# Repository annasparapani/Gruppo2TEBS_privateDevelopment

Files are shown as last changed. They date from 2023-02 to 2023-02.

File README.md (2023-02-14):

# GlucoSense&reg;  Project
## LTEBS Group 2 (2022-2023)

> NB this is the **private development** folder to use after the submission of Feb. 13th for further development that's not going to be graded. What we submitted and all the commits history before Feb. 13th is in [**this repo**](https://github.com/ltebs-polimi/AY2223_I_Project-2)

Hi! Welcome to our project repository. 
We are **Pedro Gianjoppe, Gabriele Paroli, Anna Sparapani** and **Pietro Zerboni** and we worked with or tutor Andrea Rescalli for the "Laboratorio di tecnologie elettroniche e biosensori", a course from professor Cerveri @PoliMi. 

We worked with a PSoC 5 microcontroller to develop a device that could perform Cylic Voltammetry (CV) and Chrono Amperommetry (CA) [^1] procedures with the aim to determine glucose concentration in a solution. 

In this repository you will find all the code we developed. Here's a guide on how to use the GlucoSense and after that you can find more detailed info about all the development steps and choices we made in the past months. We hope this paints a clear picture of our project, but please let us know if you have any doubts! 

###### Table of Contents 
1. [User Guide](#user-guide)
2. [Development Info](#development-info)
3. [References and Acknowledgements](#references-and-acknowledgements)

--------
## User Guide
The device presents a switch, a connector for the glucose strip and a LED. To use it you will also need a computer running the GUI. 
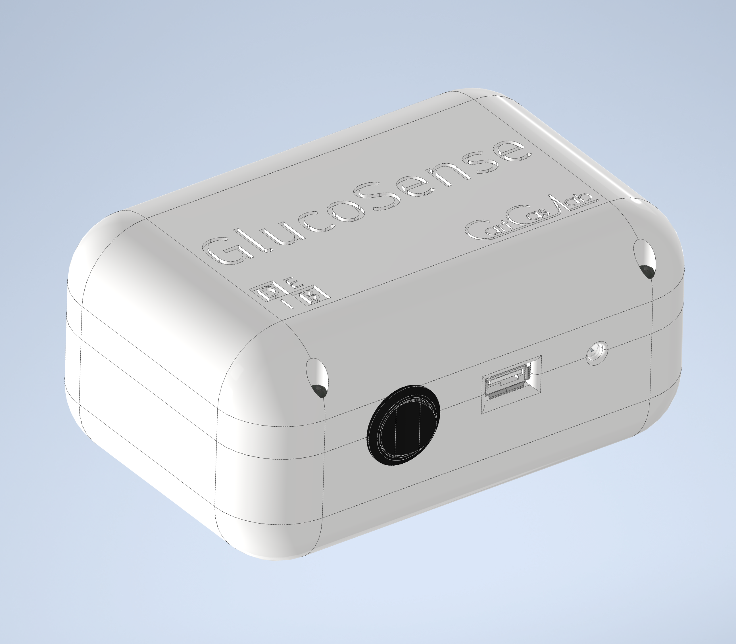
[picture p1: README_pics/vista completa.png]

1. Switch on the device, the LED should switch on
2. Start the GUI ([GUI.py](/GUI/GUI.py) file)
3. Press the `Connect to Bluetooth` button on the GUI and wait for the button to become `Disconnect from COM port`. This means that the GUI is connected to the PSoC
4. Press `TIA initialize` and wait a few seconds - *this is needed for the GUI to receive initialization data the device creates when switched on*
6. Insert a glucose strip in the connector (electrodes facing up, see [picture](#glucose-strips-and-connector))
5. Now you can start with the measurements 
   - **Option 1 : Measure Glucose**
   This allows you to perform a simple glucose measure, from the Home Screen button `Measure Glucose`. When this is pressed the device will perform a CA with standard parameters and then evaluate the glucose concentration based on the calibration curve we built.
      1. Add a drop of solution to the strip active site and make sure it turns from yellow to black
      2. Press the `Measure Glucose` button, the LED will start blinking
      3. A couple of seconds later the LED wil stop blinking and you can read the evaluated glucose concentration next to the button 
   - **Option 2 : Cyclic Voltammetry**
   This allows you to perform a CV procedure
      1. Press the `Cyclic Voltammetry` tag in the upper bar of the GUI, this will take you to the CV page
      2. Choose the parameters you want to use 
         - `Min` and `max Voltage` $\in [\pm 2500mV]$ range
         - `Scan Rate` $\in [0, 10] mV/s$ controls the speed of the procedure
         - Select the `Type of CV`, the default is a linear CV but also a Square Wave Voltammetry can be performed
         - If a SWV is chosen, select also the pulse increment and pulse height parameters
      3. Add a drop of solution to the strip active site and make sure it turns from yellow to black and wait for about 20s 
      4. Press `Start`, and wait for the procedure to finish
      5. At the end the GUI will display 
         - the graph of the measured current (mA) against the imposed voltage (mV)
         - the graph of imposed voltages (mV) against time (ms)
         - the optimal working point voltage in the bottom left corner. This is the voltage at which the biggest peak in the duck-plot is observed
   - **Option 3 : Chronoamperommetry**
      1. Press the `Chronoamperommetry` tag in the upper bar of the GUI, this will take you to the CA page
      2. Choose the parameters you want to use 
         - `Fixed Voltage` (mV) is the voltage of the low part of the square wave imposed during the CV
         - `Pulse Voltage` (mV) is the voltage of the pulse part of the CA square wave 
         - `Duration` (ms) is the period of the square wave
         - alternatively, the CA can be performed with standard parameters, which were obtained during calibration and are saved in the PSoC's EEPROM
      3. Add a drop of solution to the strip active site and make sure it turns from yellow to black and wait for about 20s 
      4. Press `Start`, and wait for the procedure to finish
      5. At the end the GUI will display 
         - the graph of the measured current (mA) against the time (ms)
         - the graph of imposed voltages (mV) against time (ms)
         - the glucose concentration based on the current at 500ms. This is accurate only if the `Pulse Voltage` is the standard one (56mV), since the calibration curve has been built with this.

If there are issues you can always disconnect and reconnect the device, as well as switching it off and then back on. Remeber that if you switch the device off, you will have to connect it again and initialize it again (pressing the `Connect to Blutooth` and `Initialize TIA` buttons). 

----
## Development Info 
1. [PsoC C Code](#1-psoc-c-code)  
   - [Files](#c-files)
   - [Interrupts](#interrupt-routines) 
2. [GUI](#2-gui)
   - [User Interface](#user-interface)
   - [Device Calibration](#device-calibration)
3. [PCB](#3-pcb)
4. [Case and Strip Interface](#4-case-and-strip-interface)
   - [Case](#case)
   - [Strip and Connector](#glucose-strips-and-connector)

Overwiew of our development stages and interactions:
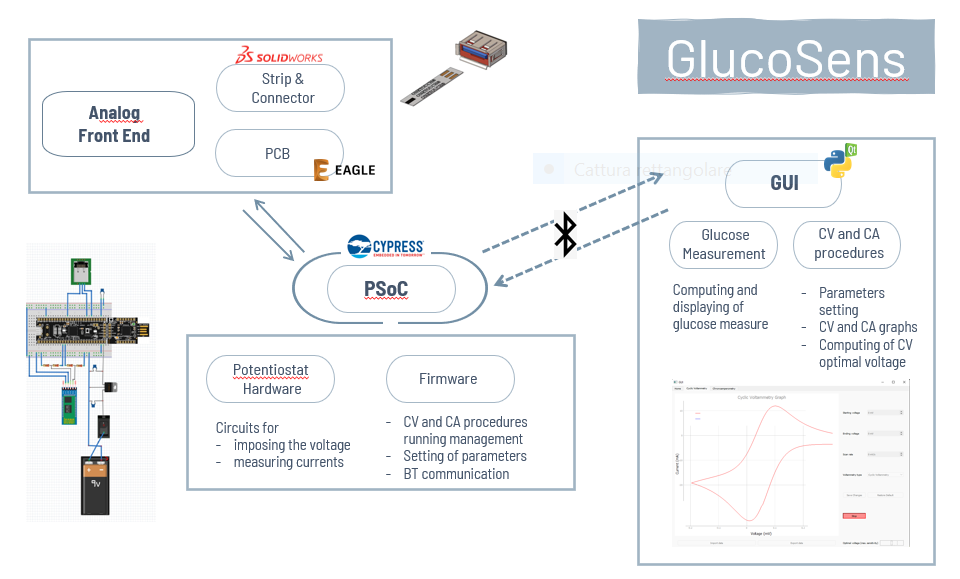
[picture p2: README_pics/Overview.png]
Overview


### 1. [PSoC C code](/PSoC_Project)
The PSoC microcontroller was programmed through its proprietary software, *PSoC creator*. The code manages all CV and CA measurements and communication with the GUI via UART Bluetooth. 
The main has a "switch cases" structure based on the input coming via BT from the GUI. Here's an example of workflow: 
1. PSoC is switched on and performs initialization procedures
2. when a byte is received on the RX of the UART BT an ISR is called, which saves it in the global variable data_buffer[]
3. when a TAIL is received on the RX of the UART BT, meaning the incoming data is finished, a flag is raised from the ISR
4. in the while(1) of the main, when the flag is raised one of the cases is entered based on data_buffer[0] and the flag is lowered
   > we are using the headers of the incoming data to switch cases in the main.c
5. the code inside the case is exectued

The code relies on a variety of .c files, which group the functions called by the main, according to their objective.

#### .c Files 

- [**`hardware_management.c`**](/PSoC_Project/PSoC_Project.cydsn/hardware_management.c) contains all functions that manage the hardware initialization, sleep, wakeup etc. during the execution of the code. The measurements and procedured rely heavily on the embedded DAC and ADC, as well as a TIA, OpAmps and other components that complete the circuit.
- [**`DAC_management.c`**](/PSoC_Project/PSoC_Project.cydsn/DAC_management.c) two DACs are be used to impose voltage (VDAC with 8 bit resolution = 16 mV resolution, and a DVDAC with 12 bits resolution ~ 1 mV resolution)
This file is called by `hardware_management.c` and simply checks which DAC is selected and performs the start, wakeup etc. function on that component (so that `hardware_management.c` does not have to check every time which DAC is selected). In our project, at this point, the user cannot select which DAC to use via GUI. Wr are always using the 8-bit VDAC; however we built the code so that for future developments, a simple change in the GUI code would allow this option.
- [**`BT_protocols.c`**](/PSoC_Project/PSoC_Project.cydsn/BT_protocols.c) this file contains the function needed to write on the BT to send data to the GUI. The reading is implemented in the BT RX ISR. 
Since when the CV and CA are performed long arrays of data have to be sent, functions in this file manage these long arrays by splitting them up in shorter arrays and sending them in consecutive iterations.
- [**`lut_protocols.c`**](/PSoC_Project/PSoC_Project.cydsn/parametric_lut.c)
the values imposed by the DAC during the procedures are either triangular waves (during CV) or a square wave (during CA). To allow a fast switching between two subsequent steps of imposing the voltage, the values are previosly saved in a Look Up Table (LUT, a global array `uint16 waveform_lut[]`). The values expressed not in mV but in levels of the DAC (255 in case of the VDAC-8 bit and 4096 in case of the DVDAC-12 bit), so they can be directly fed in input to the `DAC_SetValue(value)` API functions. 
- [**`user_inputs.c`**](/PSoC_Project/PSoC_Project.cydsn/user_inputs.c) this file contains functions that are often called by the `main.c` cases and act as a midman between the main and the technical functions contained in the previously discussed files.

#### Interrupt Routines 
- **`dacInterrupt`** called on the rising edge of the PWM wave during the CV and CA procedures, it imposes a DAC value on the counter electrode. It uses the `DAC_SetValue(uint8 value)` API function, and the input is given as a level of the DAC. The conversion from mV to DAC levels is perfomed in the GUI before sending the parameters, so that the LUT is already built in terms of DAC levels.
When the measure is finished (all the wave saved in the LUT has been imposed) it sends the data to the GUI via BT.
- **`adcInterrupt`** called on the falling edge of the PWM wave during CV and CA procedures, it reads the voltage at the working electrode and saves in in th global array `data_long[]` which will be send to the GUI at the end of the procedure.
   > **PWM called ISRs** \\
   the `dacInterrupt` and the `adcInterrupt` are called on the falling and rising edges od the PWM squared wave respectively. Since the user can selected the *Scan Rate* parammeter in the CV procedure, the speed at which the traingular wave is imposed needs to the changed. To allow this, we adapt the PWM period to the scan rate (done by a function from `user_inputs.c`)
- **`Custom_UART_BT_RX_Interrupt`** manages the RX of the BT UART. It is called every time there is an incoming byte on the RX and saves the data in the global array `data_buffer[]`. When byte equals to `TAIL` is received, it raises a flag to signal the main that there is some ready data.

### 2. GUI
#### User Interface
The Graphical User Interface (GUI) has been implemented in Python - `PyQt5`. To run it you just need to open the [GUI.py](/GUI/GUI.py) file in the GUI folder and run the .py code using the PyQt virtual environment. It is necessary to install the [`scipy`](https://pypi.org/project/scipy/), [`PyQt5`](https://pypi.org/project/PyQt5/), [`pyqtgraph`](https://pypi.org/project/pyqtgraph/), [`pyserial`](https://pypi.org/project/pyserial/) and `serial` libraries to run the code.

The GUI performs all interactions between the user (which is the patient or the doctor) and the device, since there are no buttons or LCD screens in the hardware except from the turn ON / OFF button, which can be used to restart the PSoC.

Those interactions are implemented by serial communication between the Bluetooth Module connected to PSoC and the Python `serial` library. Multithreading in PyQt was implemented to establish the connection of the COM port and also for the reading and writing data from PyQt to Bluetooth.

The GUI is divided in 3 different tabs: "Home screen", "Cyclic voltametry" and "Chronoamperometry", each one with its own funcionalities and widgets.

##### 1. Home screen
performs bluetooth connection and one-click glucose measurement (only page that the patient can access).



When the GUI is started, the connection is switched on by pressing the `Connect to Bluetooth` button which triggers the GUI to scan all serial ports by sending a specific character. When the serial port corresponding to the PSoC BT module responds with the proper character, the port is opened and the device results connected to the GUI. After that, the `TIA initialize` button is used to signal the PSoC that it can send back the values from the initialization of the TIA, in order for the GUI to calculate and store the TIA resistance value.

Below, in this same screen, the `Measure Glucose` button to performs the one-click glucose concentration measurement by performing Chronoamperometry with the default parameters stored found during calibration. Then, the proper current value is retrieved from the measurement and applied to the linear regression model obtained from the calibration of the device. The resulting value, corresponding to the glucose concentration, is displayed.

##### 2. Cyclic Voltammetry
performs and displays Cyclic or Square-Wave Voltammetry procedures with desired parameters, imports and exports measurements to external .csv files and computes optimal voltage for Chronoamperometry 
> Our idea is that this page is accessed only by a clinician who knows how to set the parameters. The patient only uses the Home page and performs simple glucose measurements.



In the CV screen, the user can choose the CV parameters (*scan rate, start and end values, type of CV*) and start the procedure. It is also possible to save the parameters in the EEPROM (`Save changes`) and retrieve parameters from the EEPROM (`Restore default`).

When the procedure button (`Start`) is pressed, the parameters are sent to the PSoC, which creates the LUT and adapts the period of the PWM. It then starts the procedure and it is possible to interrupt the measurements by pressing the same button (which now displays the label `Stop` in red). When the procedure is finished (in case it is not interrupted by the user), PSoC sends all measured values back to the GUI. The GUI receives two arrays, the first with all measured voltages and the second with the LUT (all imposed voltages), converts the values in mA and mV ranges and then plots them in two graphs: 
- The duck-plot of the Current (mA) in respect to the imposed Voltage (mV)
   > we tested the device, and obtained duck-plots for concentrations in the [50, 200] mg/L range. If you use a much higher or lower concentration the parameters the GUI allows you to choose will probably not lead to a duck-plot.
- The imposed Voltage (mV) with respect to the procedure time (ms) 

It also retrieves the optimal voltage for the Chronoamperometry by computing the value of imposed voltage for which we have the highest current measurement in absolute value (the highest or lowest peak in the duck-plot).

#### 3. Chrono Amperometry
performs and displays ChronoAmperometry procedure with desired parameters, imports and exports measurements to external file and computes the Glucose Concentration (page accessed only by the doctor).
> As for the CV page, our idea is that this page is accessed only by a clinician who knows how to set the parameters.



Very similar to the CV screen, the CA screen allows selection of CA parameters and starting of procedure and then plots the measurements data coming from the PSoC in two graphs: 
- The exponential decay plot of the Current (mA) in respect to the procedure Time (ms)
   > as for the CV, we tested the device for concentrations in the [50, 200] mg/L range.
- The imposed Voltage (mV) in respect to the to the procedure Time (ms)

It also calculates the glucose concentration by retrieving the proper current value from the measurements and appling it to the linear regression model obtained from the [calibration](#device-calibration) of the device. The resulting value, corresponding to the glucose concentration, is displayed.

Both CV and CA screens allow for **export** and **import** of data. 
- Data is exported into a `.csv` file and named with the time and date of the measure. 
- Data can be imported to be graphed in the corresponding window

Both CV and CA screens allow to **Save changes to EEPROM** and also to retrieve the **default values from EEPROM**.

#### DEVICE CALIBRATION
In order to allow the computation of the glucose concentration by means of the CA measurements, a calibration step was necessary for the device. The calibration was done using the GUI and followed the steps:
1. Perform Cyclic Voltammetry procedure to find the optimal voltage as the imposed voltage for which the measured current has maximum magnitude 

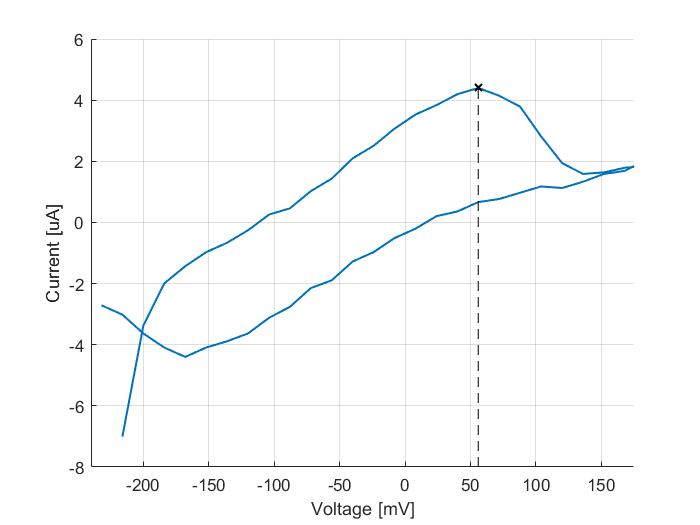
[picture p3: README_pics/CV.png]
CV to find the optimal voltage
   
   The optimal voltage was found at **56mV**

2. Set up the parameter `Pulse Voltage (ms)` of the CA as the optimal voltage from the CV

3. Perform CA procedure for 4 different solutions with known glucose concentration (50, 100, 150 and 200 mg / dL) 

4. For each resulting graph of Current (mA) over Time (ms), retrieve the current measurement at a st time stamp (current measured at 500 ms, so the 50th value, since the CA is performed with 10ms intervals) to be used in the linear regression.
Here are the current vs time graphs we obtained: 
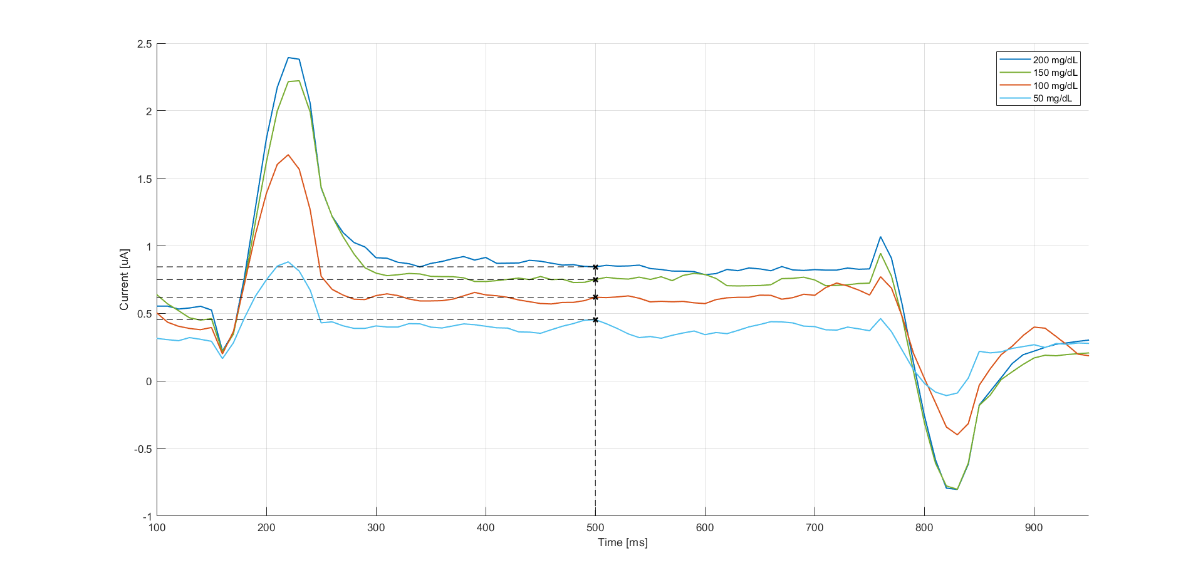
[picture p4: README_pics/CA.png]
CA for 4 glucose concentrations


6. Plot the 4 values of current measured at 500ms with respect to the known glucose concentration

7. Apply Linear Regression to find the **Calibration curve** of the device 
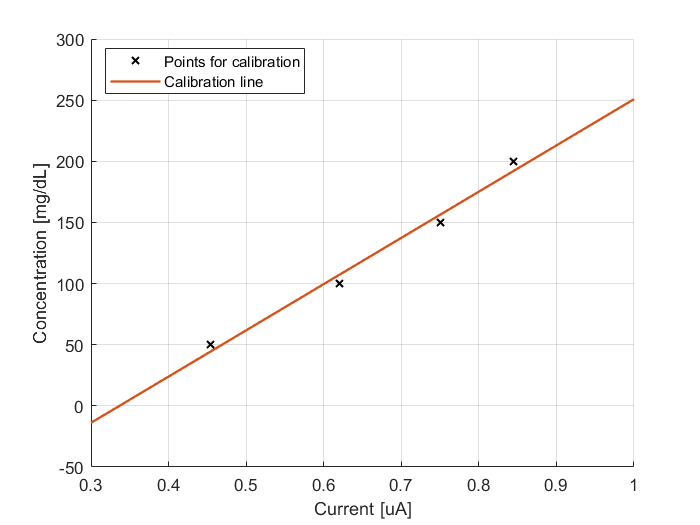
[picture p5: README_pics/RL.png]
Calibration curve


These plots and the linear regression were done in *MatLab*.

### 3. [PCB](/PCB)
Most of the electrical design needed to perform the procedures is embedded in the PSoC (DACs, ADC, TIA etc.), so the PCB only presents interface elements. 
The PCB was developed in *Eagle* by Autodesk. Here is a simplified schematic created on *Fritzing*:

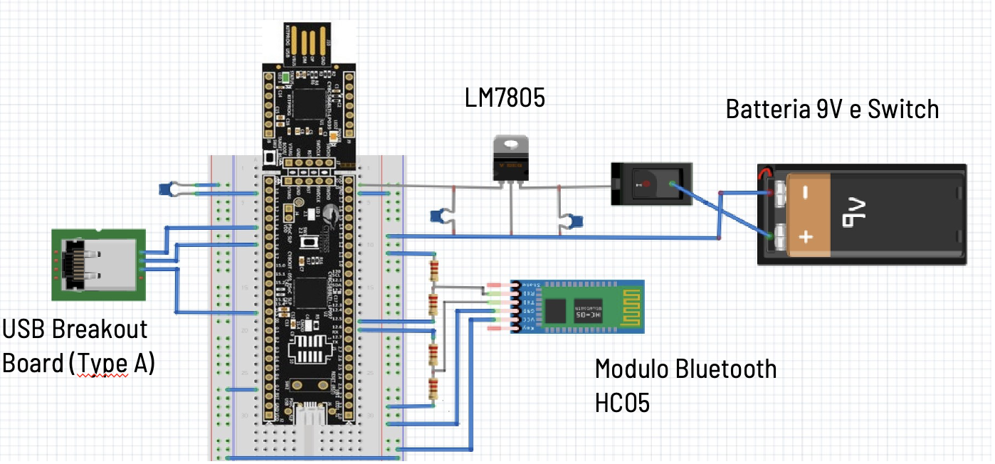
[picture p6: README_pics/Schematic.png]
Fritzing Schematic


As you can see from the image, the board includes:
1. Connections for the BT module. We use a voltage divider to lower the voltage as the TX and RX pins works at 3,3V.
2. The USB breakout board, used to interface the glucose strip with the board
3. One LED
3. The power circuit, we use a 9V DC battery and a standard linearization circuit and a switch (so that the device doesn't need to be connected to the computer running the GUI or to any other power source)

We self made the board in the lab, printing the Eagle schematic and then imprinting it on a copper covered board. We then cut it and pierced it to solder the components. We soldered directly only resistances and capacitors, and placed plugs for all other elements, so that they can be easily removed and reused by the lab.

Here's an image of our printed board 
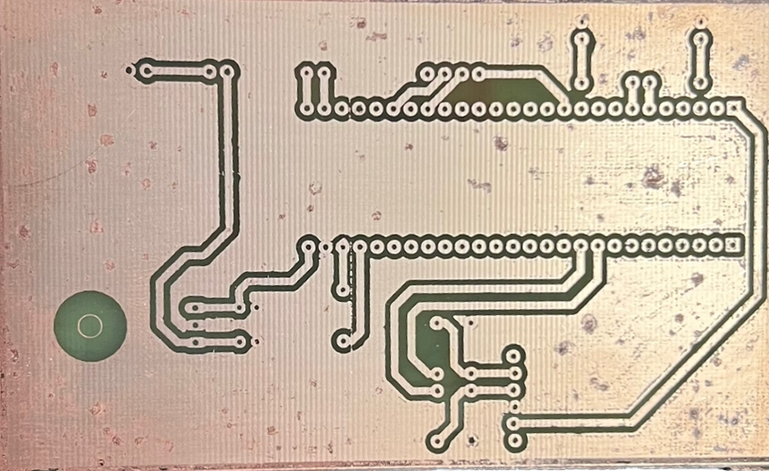
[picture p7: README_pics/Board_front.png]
Board
 

and here the back with the elements soldered on
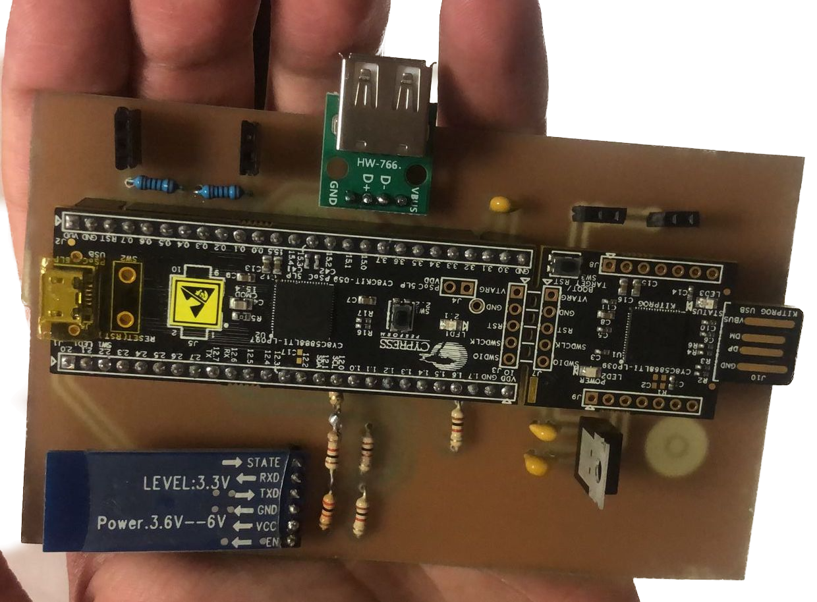
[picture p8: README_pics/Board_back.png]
Board
 

### 4. [Case and strip interface](/3D/)
Our idea for the case was to have a clean design with only the essential interface elements on the outside. As you can see from the following pics the device presents itself as a box with a switch, connector for the glucose strip, and a LED on the side. 
All 3D modeling was performed using *Autodesk Inventor*, followed by slicing of all parts using *Cura* software. Finally, the parts were 3D printed in PLA using an *Ultimaker 3*.

#### Case
The case was designed and constructed to be compact while allowing separate and easy access to both the PSoC and battery. The PSoC can be accessed by removing the four screws holding the top portion of the case in place, providing access to the PCB and components soldered onto it. 
A dedicated compartment was created in the lower portion of the case to hold the battery, and access to it can be obtained by removing a cover held in place by two screws.
Case Open
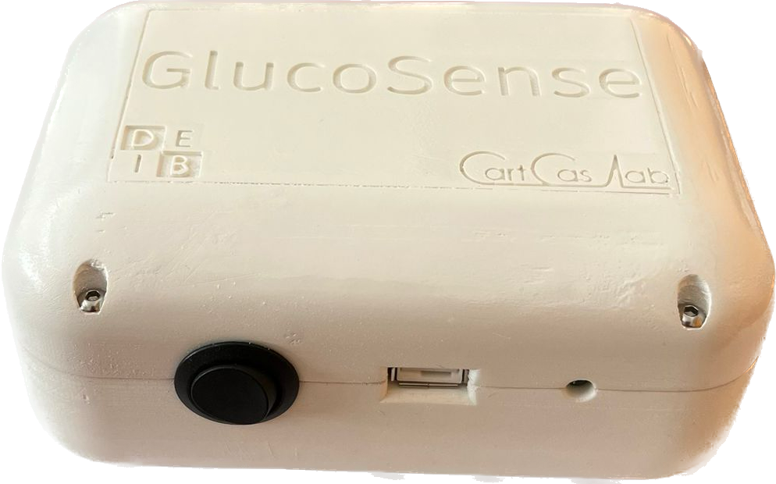
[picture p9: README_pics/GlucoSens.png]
GlucoSens


#### Glucose strips and connector 
We chose the [*OneTouch Ultra*](https://www.amazon.it/One-Touch-Ultra-Strisce-Test/dp/B002FU5WHY/ref=sr_1_1?keywords=one+touch+ultra+strisce&qid=1676288893&sr=8-1) glucose strips to develop our device around. They are readily available on Amazon, quite cheap and provide three electrodes easily accessible. 

To have an easy and realiable way to interface the strips with the device electrical pins, we decided to adapt a female USB connector so that three out of four of the electrical lines of the USB would turn into our electrodes lines.
We designed and 3D printed a custom adapter, which leaves the correct space to insert the strip and ensures electrical contact of the electrodes on the strip with three electrodes of the USB, as you can see from the following diagram.
Connector

---
### References and Acknowledgements

Our work was inspired by the previous work of Lopin et al. (2018) [^2], which proposed to use the PSoC as a potentiostat and developed PSoC anf GUI code to perform CV and CA procedures.
Our requirements differ in some ways from the aim of Lopin et al., so we had to adapt and change significantly our development, but their code was of great help.

For the choice of the OneTouch Ultra as for glucose strips, we relied on the project by M. Bindhammer, published on *hackaday.io* [^3]. The project is then developed on an ArduinoUNO microcontroller. 

We would like to thank our tutor Andrea Rescalli for his help and insights, as well as the lab's team. 

[^1]:"A Practical Beginner’s Guide to Cyclic Voltammetry"
Noémie Elgrishi, Kelley J. Rountree, Brian D. McCarthy, Eric S. Rountree, Thomas T. Eisenhart, and Jillian L. Dempsey
Journal of Chemical Education 2018 95 (2), 197-206
DOI: 10.1021/acs.jchemed.7b00361

[^2]:"PSoC-Stat: A single chip open source potentiostat based on a Programmable System on a Chip"
Lopin P, Lopin KV (2018) PSoC-Stat: A single chip open source potentiostat based on a Programmable System on a Chip. PLOS ONE 13(7): e0201353. https://doi.org/10.1371/journal.pone.0201353 

[^3]:https://hackaday.io/project/11719-open-source-arduino-blood-glucose-meter-shield
# Gruppo2TEBS_privateDevelopment

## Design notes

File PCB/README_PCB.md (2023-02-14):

## READ ME - PCB

PCB mono layer.

### SCHEMATICO:
-Spostare SWTICH1 sulla SX in modo che sia accanto alla brakout board -> altrimenti dobbiamo tirare dei jumper oltre la scheda

### BOARD:
- IMpostato uno spacing di almeno 1mm tra route e ground plane
- SWITCH1 da sposatre
- BLE_MODULE, il pin 1 e 6 non ci servono

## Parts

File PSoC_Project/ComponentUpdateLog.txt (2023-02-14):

Last Modified Date & Time: 01/15/2023 09:01:02

PSoC_Project: PSoC_Project.cydwr
	LIN_Dynamic [v5.0] to [v6.0]

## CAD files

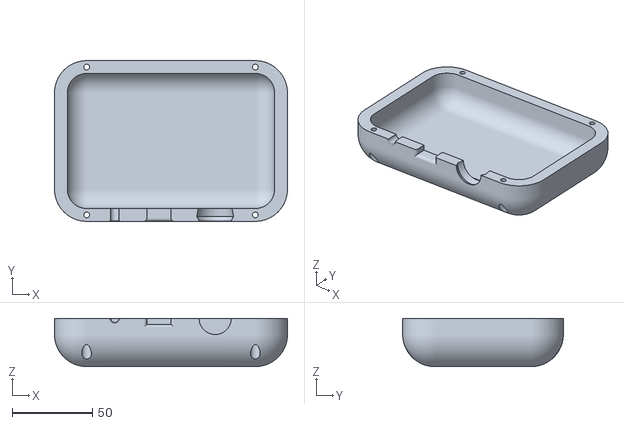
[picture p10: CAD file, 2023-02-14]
3D/Case - Cura/Case superiore.stl
145.0 x 100.0 x 30.0

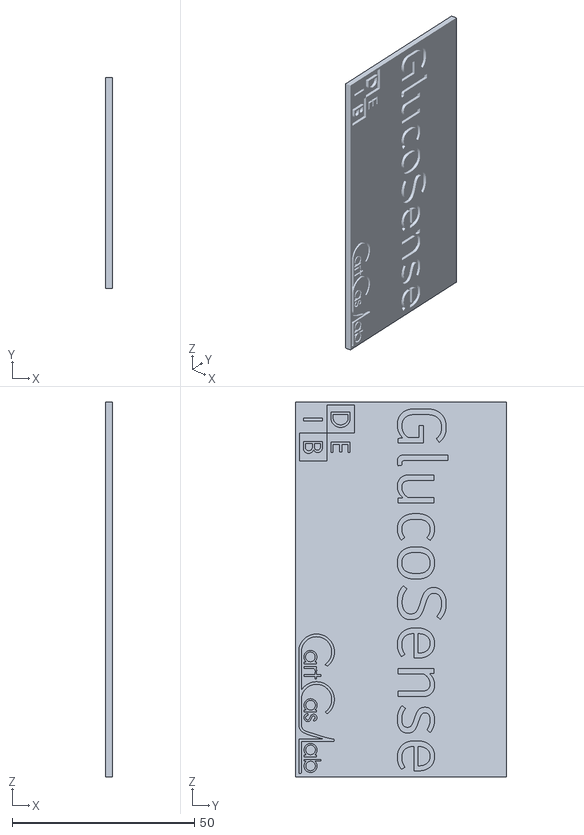
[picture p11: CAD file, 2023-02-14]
3D/Case - Cura/Targhetta.stl
2.00 x 58.0 x 103.0

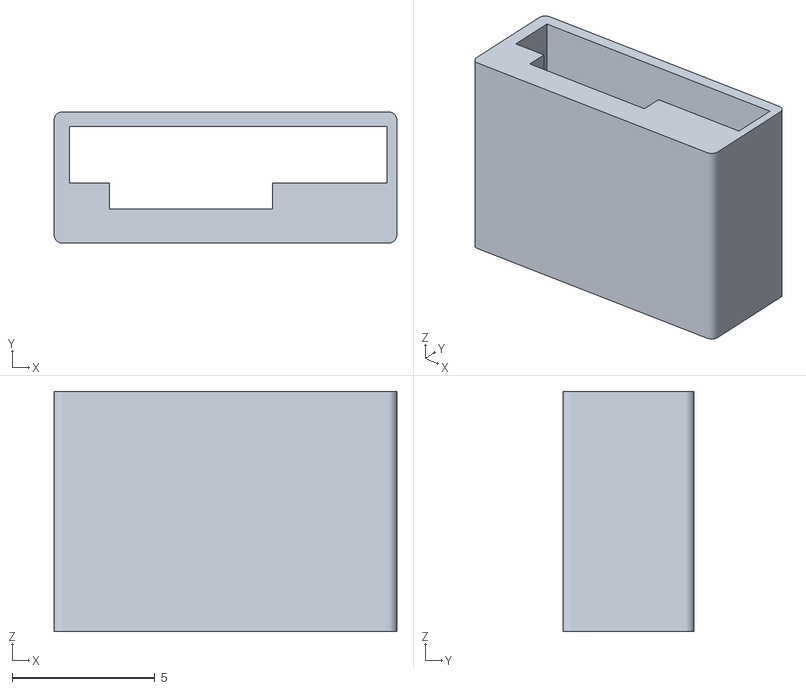
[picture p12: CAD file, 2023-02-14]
3D/Case - Cura/Adattatore.stl
12.0 x 4.60 x 8.40

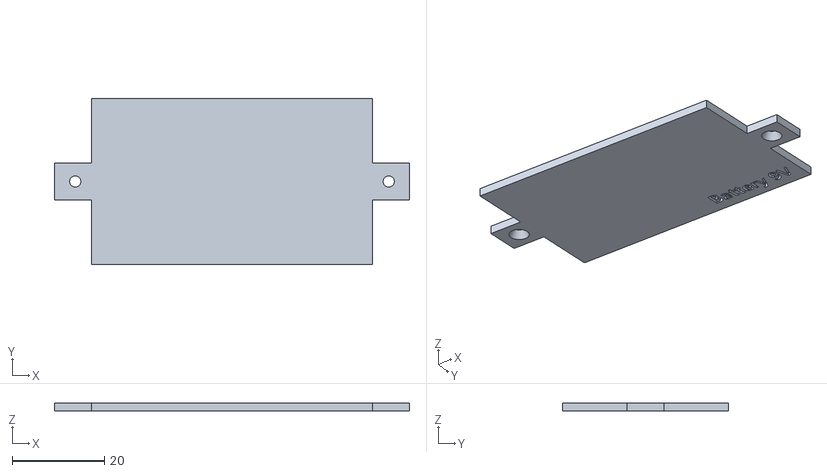
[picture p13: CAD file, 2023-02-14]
3D/Case - Cura/Coperchio.stl
77.0 x 36.0 x 1.80

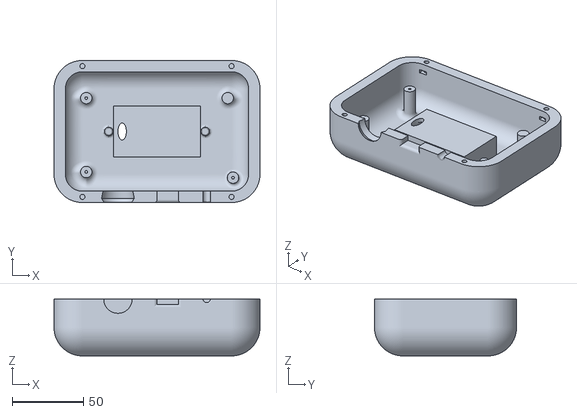
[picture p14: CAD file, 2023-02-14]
3D/Case - Cura/Case inferiore.stl
145.0 x 100.0 x 40.0

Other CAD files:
3D/Case - Inventor/5mm LED Transparent.ipt
3D/Case - Inventor/9V Battery Clip Connector.ipt
3D/Case - Inventor/9V Battery.ipt
3D/Case - Inventor/Adattatore.ipt
3D/Case - Inventor/Batteria e connettore.iam
3D/Case - Inventor/Board connector.ipt
3D/Case - Inventor/Case inferiore completo.iam
3D/Case - Inventor/Case inferiore e batteria.iam
3D/Case - Inventor/Case inferiore.ipt
3D/Case - Inventor/Case superiore.ipt
3D/Case - Inventor/Connettore adattatore e strip.iam
3D/Case - Inventor/Connettore e adattatore.iam
3D/Case - Inventor/Coperchio.ipt
3D/Case - Inventor/HC-05.ipt
3D/Case - Inventor/L7805.ipt
3D/Case - Inventor/OldVersions/Adattatore.0001.ipt
3D/Case - Inventor/OldVersions/Adattatore2.0001.ipt
3D/Case - Inventor/OldVersions/Batteria e connettore.0001.iam
3D/Case - Inventor/OldVersions/Case inferiore completo.0015.iam
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

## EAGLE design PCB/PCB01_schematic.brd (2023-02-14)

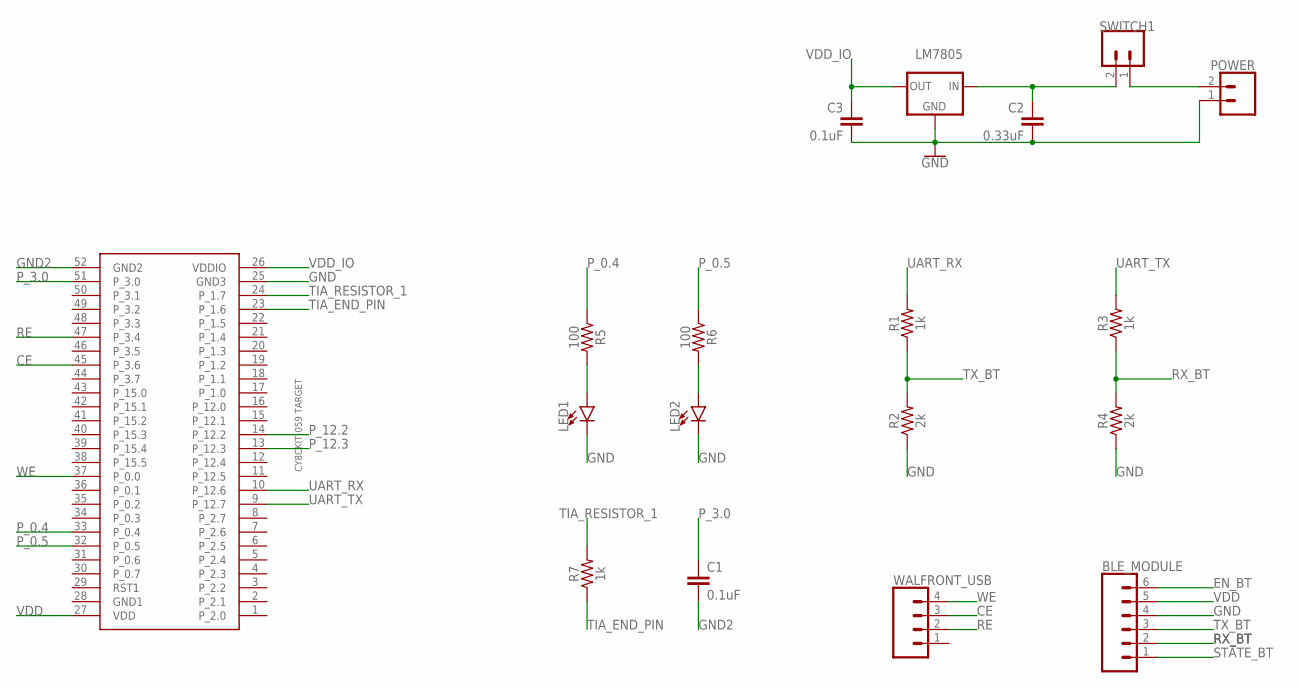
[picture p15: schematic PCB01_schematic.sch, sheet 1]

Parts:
BLE_MODULE: CONN_06LOCK; 1X06_LOCK
C1, C3: 0.1uF; C2.5-2
C2: 0.33uF; C2.5-2
LED1, LED2: LED3MM; LED_3MM
LM7805: V_REG_78XXSIDE; 78XXL
POWER: CONN_02; 1X02
R1, R3, R7: 1k; AXIAL-0.3
R2, R4: 2k; AXIAL-0.3
R5, R6: 100; AXIAL-0.3
SWITCH1: CONN_02; 1X02
U$2: CY8CKIT-059_TARGET_3
WALFRONT_USB: CONN_04; 1X04

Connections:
CE: U$2.45 (P_3.6), WALFRONT_USB.3
EN_BT: BLE_MODULE.6
GND: BLE_MODULE.4, C2.2, C3.2, LED1.K (C), LED2.K (C), LM7805.GND, POWER.1, R2.P$1 (1), R4.P$1 (1), U$2.25 (GND3)
GND1: U$2.28 (GND1)
GND2: C1.2, U$2.52 (GND2)
unnamed: C2.1, LM7805.IN, SWITCH1.2
unnamed: POWER.2, SWITCH1.1
unnamed: LED1.A, R5.P$2 (2)
unnamed: LED2.A, R6.P$2 (2)
P_0.4: R5.P$1 (1), U$2.33 (P_0.4)
P_0.5: R6.P$1 (1), U$2.32 (P_0.5)
P_3.0: C1.1, U$2.51 (P_3.0)
P_12.2: U$2.14 (P_12.2)
P_12.3: U$2.13 (P_12.3)
RE: U$2.47 (P_3.4), WALFRONT_USB.2
RX_BT: BLE_MODULE.2, R3.P$1 (1), R4.P$2 (2)
STATE_BT: BLE_MODULE.1
TIA_END_PIN: R7.P$1 (1), U$2.23 (P_1.6)
TIA_RESISTOR_1: R7.P$2 (2), U$2.24 (P_1.7)
TX_BT: BLE_MODULE.3, R1.P$1 (1), R2.P$2 (2)
UART_RX: R1.P$2 (2), U$2.10 (P_12.6)
UART_TX: R3.P$2 (2), U$2.9 (P_12.7)
VDD: BLE_MODULE.5, U$2.27 (VDD)
VDD_IO: C3.1, LM7805.OUT, U$2.26 (VDDIO)
WE: U$2.37 (P_0.0), WALFRONT_USB.4

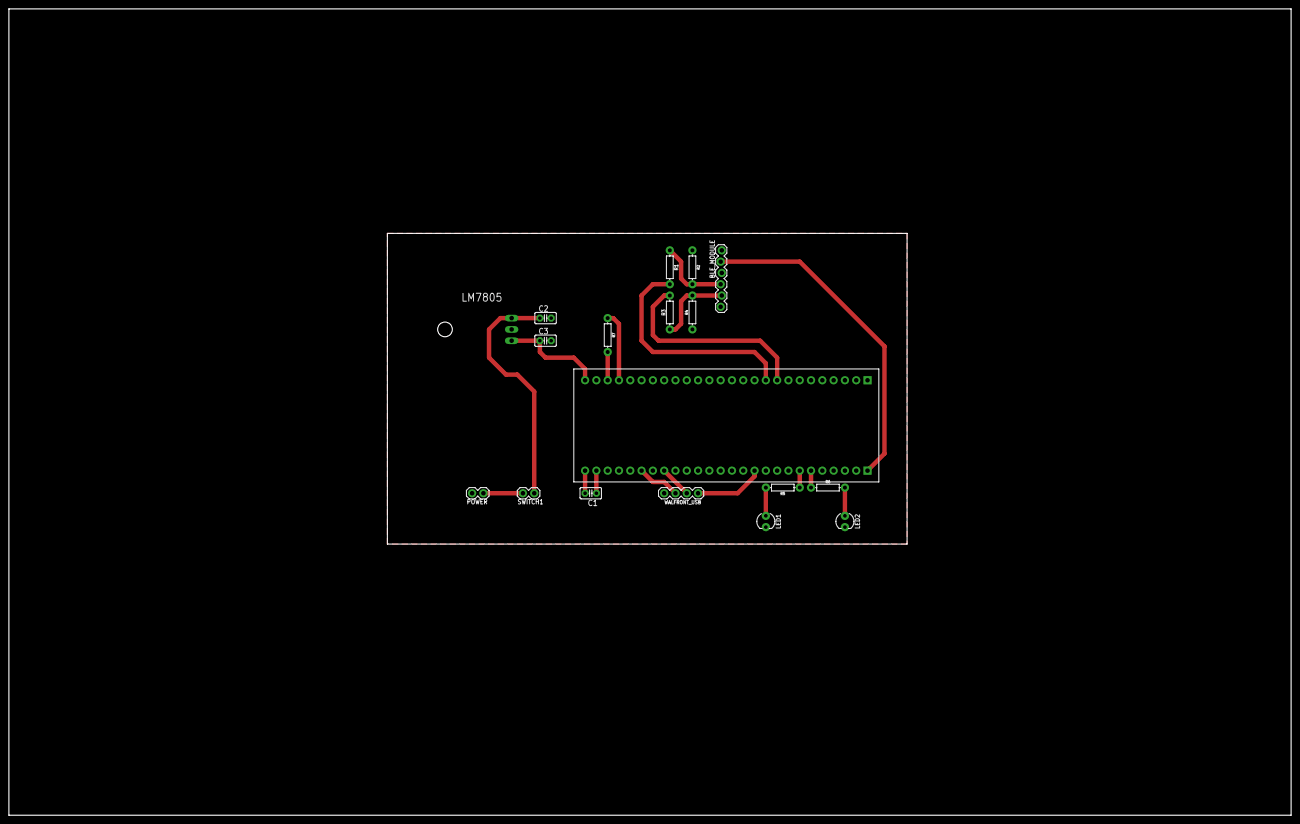
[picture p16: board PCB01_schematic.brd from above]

Board: 2 copper layers, 288.3 x 181.3 mm, 18 parts (1 on the bottom side), 20 nets.

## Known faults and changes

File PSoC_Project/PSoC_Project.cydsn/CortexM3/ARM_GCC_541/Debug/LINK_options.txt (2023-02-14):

-Wl,--start-group -o "\\\\.psf\\Home\\Desktop\\LAB_TEBS\\_Progetto\\TEBS_GitHub\\PSoC_Project\\PSoC_Project.cydsn\\CortexM3\\ARM_GCC_541\\Debug\\PSoC_Project.elf" ".\\CortexM3\\ARM_GCC_541\\Debug\\main.o" ".\\CortexM3\\ARM_GCC_541\\Debug\\TIA_calibrate.o" ".\\CortexM3\\ARM_GCC_541\\Debug\\user_inputs.o" ".\\CortexM3\\ARM_GCC_541\\Debug\\hardware_management.o" ".\\CortexM3\\ARM_GCC_541\\Debug\\parametric_lut.o" ".\\CortexM3\\ARM_GCC_541\\Debug\\DAC_management.o" ".\\CortexM3\\ARM_GCC_541\\Debug\\BT_protocols.o" ".\\CortexM3\\ARM_GCC_541\\Debug\\cyfitter_cfg.o" ".\\CortexM3\\ARM_GCC_541\\Debug\\cymetadata.o" ".\\CortexM3\\ARM_GCC_541\\Debug\\Cm3Start.o" ".\\CortexM3\\ARM_GCC_541\\Debug\\PSoC_Project.a" "C:\\Program\ Files\ (x86)\\Cypress\\PSoC\ Creator\\4.4\\PSoC\ Creator\\psoc\\content\\cycomponentlibrary\\CyComponentLibrary.cylib\\CortexM3\\ARM_GCC_541\\Debug\\CyComponentLibrary.a" -mcpu=cortex-m3 -mthumb -L "Generated_Source\\PSoC5" "-Wl,-Map,.\\CortexM3\\ARM_GCC_541\\Debug/PSoC_Project.map" -T "Generated_Source\\PSoC5\\cm3gcc.ld" -specs=nano.specs -Wl,--gc-sections -g -ffunction-sections -Og -ffat-lto-objects -Wl,--end-group

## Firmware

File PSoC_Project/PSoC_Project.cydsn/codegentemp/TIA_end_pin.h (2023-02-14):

/*******************************************************************************
* File Name: TIA_end_pin.h  
* Version 2.20
*
* Description:
*  This file contains Pin function prototypes and register defines
*
* Note:
*
********************************************************************************
* Copyright 2008-2015, Cypress Semiconductor Corporation.  All rights reserved.
* You may use this file only in accordance with the license, terms, conditions, 
* disclaimers, and limitations in the end user license agreement accompanying 
* the software package with which this file was provided.
*******************************************************************************/

#if !defined(CY_PINS_TIA_end_pin_H) /* Pins TIA_end_pin_H */
#define CY_PINS_TIA_end_pin_H

#include "cytypes.h"
#include "cyfitter.h"
#include "cypins.h"
#include "TIA_end_pin_aliases.h"

/* APIs are not generated for P15[7:6] */
#if !(CY_PSOC5A &&\
	 TIA_end_pin__PORT == 15 && ((TIA_end_pin__MASK & 0xC0) != 0))


/***************************************
*        Function Prototypes             
***************************************/    

/**
* \addtogroup group_general
* @{
*/
void    TIA_end_pin_Write(uint8 value);
void    TIA_end_pin_SetDriveMode(uint8 mode);
uint8   TIA_end_pin_ReadDataReg(void);
uint8   TIA_end_pin_Read(void);
void    TIA_end_pin_SetInterruptMode(uint16 position, uint16 mode);
uint8   TIA_end_pin_ClearInterrupt(void);
/** @} general */

/***************************************
*           API Constants        
***************************************/
/**
* \addtogroup group_constants
* @{
*/
    /** \addtogroup driveMode Drive mode constants
     * \brief Constants to be passed as "mode" parameter in the TIA_end_pin_SetDriveMode() function.
     *  @{
     */
        #define TIA_end_pin_DM_ALG_HIZ         PIN_DM_ALG_HIZ
        #define TIA_end_pin_DM_DIG_HIZ         PIN_DM_DIG_HIZ
        #define TIA_end_pin_DM_RES_UP          PIN_DM_RES_UP
        #define TIA_end_pin_DM_RES_DWN         PIN_DM_RES_DWN
        #define TIA_end_pin_DM_OD_LO           PIN_DM_OD_LO
        #define TIA_end_pin_DM_OD_HI           PIN_DM_OD_HI
        #define TIA_end_pin_DM_STRONG          PIN_DM_STRONG
        #define TIA_end_pin_DM_RES_UPDWN       PIN_DM_RES_UPDWN
    /** @} driveMode */
/** @} group_constants */
    
/* Digital Port Constants */
#define TIA_end_pin_MASK               TIA_end_pin__MASK
#define TIA_end_pin_SHIFT              TIA_end_pin__SHIFT
#define TIA_end_pin_WIDTH              1u

/* Interrupt constants */
#if defined(TIA_end_pin__INTSTAT)
/**
* \addtogroup group_constants
* @{
*/
    /** \addtogroup intrMode Interrupt constants
     * \brief Constants to be passed as "mode" parameter in TIA_end_pin_SetInterruptMode() function.
     *  @{
     */
        #define TIA_end_pin_INTR_NONE      (uint16)(0x0000u)
        #define TIA_end_pin_INTR_RISING    (uint16)(0x0001u)
        #define TIA_end_pin_INTR_FALLING   (uint16)(0x0002u)
        #define TIA_end_pin_INTR_BOTH      (uint16)(0x0003u) 
    /** @} intrMode */
/** @} group_constants */

    #define TIA_end_pin_INTR_MASK      (0x01u) 
#endif /* (TIA_end_pin__INTSTAT) */


/***************************************
*             Registers        
***************************************/

/* Main Port Registers */
/* Pin State */
#define TIA_end_pin_PS                     (* (reg8 *) TIA_end_pin__PS)
/* Data Register */
#define TIA_end_pin_DR                     (* (reg8 *) TIA_end_pin__DR)
/* Port Number */
#define TIA_end_pin_PRT_NUM                (* (reg8 *) TIA_end_pin__PRT) 
/* Connect to Analog Globals */                                                  
#define TIA_end_pin_AG                     (* (reg8 *) TIA_end_pin__AG)                       
/* Analog MUX bux enable */
#define TIA_end_pin_AMUX                   (* (reg8 *) TIA_end_pin__AMUX) 
/* Bidirectional Enable */                                                        
#define TIA_end_pin_BIE                    (* (reg8 *) TIA_end_pin__BIE)
/* Bit-mask for Aliased Register Access */
#define TIA_end_pin_BIT_MASK               (* (reg8 *) TIA_end_pin__BIT_MASK)
/* Bypass Enable */
#define TIA_end_pin_BYP                    (* (reg8 *) TIA_end_pin__BYP)
/* Port wide control signals */                                                   
#define TIA_end_pin_CTL                    (* (reg8 *) TIA_end_pin__CTL)
/* Drive Modes */
#define TIA_end_pin_DM0                    (* (reg8 *) TIA_end_pin__DM0) 
#define TIA_end_pin_DM1                    (* (reg8 *) TIA_end_pin__DM1)
#define TIA_end_pin_DM2                    (* (reg8 *) TIA_end_pin__DM2) 
/* Input Buffer Disable Override */
#define TIA_end_pin_INP_DIS                (* (reg8 *) TIA_end_pin__INP_DIS)
/* LCD Common or Segment Drive */
#define TIA_end_pin_LCD_COM_SEG            (* (reg8 *) TIA_end_pin__LCD_COM_SEG)
/* Enable Segment LCD */
#define TIA_end_pin_LCD_EN                 (* (reg8 *) TIA_end_pin__LCD_EN)
/* Slew Rate Control */
#define TIA_end_pin_SLW                    (* (reg8 *) TIA_end_pin__SLW)

/* DSI Port Registers */
/* Global DSI Select Register */
#define TIA_end_pin_PRTDSI__CAPS_SEL       (* (reg8 *) TIA_end_pin__PRTDSI__CAPS_SEL) 
/* Double Sync Enable */
#define TIA_end_pin_PRTDSI__DBL_SYNC_IN    (* (reg8 *) TIA_end_pin__PRTDSI__DBL_SYNC_IN) 
/* Output Enable Select Drive Strength */
#define TIA_end_pin_PRTDSI__OE_SEL0        (* (reg8 *) TIA_end_pin__PRTDSI__OE_SEL0) 
#define TIA_end_pin_PRTDSI__OE_SEL1        (* (reg8 *) TIA_end_pin__PRTDSI__OE_SEL1) 
/* Port Pin Output Select Registers */
#define TIA_end_pin_PRTDSI__OUT_SEL0       (* (reg8 *) TIA_end_pin__PRTDSI__OUT_SEL0) 
#define TIA_end_pin_PRTDSI__OUT_SEL1       (* (reg8 *) TIA_end_pin__PRTDSI__OUT_SEL1) 
/* Sync Output Enable Registers */
#define TIA_end_pin_PRTDSI__SYNC_OUT       (* (reg8 *) TIA_end_pin__PRTDSI__SYNC_OUT) 

/* SIO registers */
#if defined(TIA_end_pin__SIO_CFG)
    #define TIA_end_pin_SIO_HYST_EN        (* (reg8 *) TIA_end_pin__SIO_HYST_EN)
    #define TIA_end_pin_SIO_REG_HIFREQ     (* (reg8 *) TIA_end_pin__SIO_REG_HIFREQ)
    #define TIA_end_pin_SIO_CFG            (* (reg8 *) TIA_end_pin__SIO_CFG)
    #define TIA_end_pin_SIO_DIFF           (* (reg8 *) TIA_end_pin__SIO_DIFF)
#endif /* (TIA_end_pin__SIO_CFG) */

/* Interrupt Registers */
#if defined(TIA_end_pin__INTSTAT)
    #define TIA_end_pin_INTSTAT            (* (reg8 *) TIA_end_pin__INTSTAT)
    #define TIA_end_pin_SNAP               (* (reg8 *) TIA_end_pin__SNAP)
    
	#define TIA_end_pin_0_INTTYPE_REG 		(* (reg8 *) TIA_end_pin__0__INTTYPE)
#endif /* (TIA_end_pin__INTSTAT) */

#endif /* CY_PSOC5A... */

#endif /*  CY_PINS_TIA_end_pin_H */


/* [] END OF FILE */

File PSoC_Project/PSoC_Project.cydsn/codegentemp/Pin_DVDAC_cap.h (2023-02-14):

/*******************************************************************************
* File Name: Pin_DVDAC_cap.h  
* Version 2.20
*
* Description:
*  This file contains Pin function prototypes and register defines
*
* Note:
*
********************************************************************************
* Copyright 2008-2015, Cypress Semiconductor Corporation.  All rights reserved.
* You may use this file only in accordance with the license, terms, conditions, 
* disclaimers, and limitations in the end user license agreement accompanying 
* the software package with which this file was provided.
*******************************************************************************/

#if !defined(CY_PINS_Pin_DVDAC_cap_H) /* Pins Pin_DVDAC_cap_H */
#define CY_PINS_Pin_DVDAC_cap_H

#include "cytypes.h"
#include "cyfitter.h"
#include "cypins.h"
#include "Pin_DVDAC_cap_aliases.h"

/* APIs are not generated for P15[7:6] */
#if !(CY_PSOC5A &&\
	 Pin_DVDAC_cap__PORT == 15 && ((Pin_DVDAC_cap__MASK & 0xC0) != 0))


/***************************************
*        Function Prototypes             
***************************************/    

/**
* \addtogroup group_general
* @{
*/
void    Pin_DVDAC_cap_Write(uint8 value);
void    Pin_DVDAC_cap_SetDriveMode(uint8 mode);
uint8   Pin_DVDAC_cap_ReadDataReg(void);
uint8   Pin_DVDAC_cap_Read(void);
void    Pin_DVDAC_cap_SetInterruptMode(uint16 position, uint16 mode);
uint8   Pin_DVDAC_cap_ClearInterrupt(void);
/** @} general */

/***************************************
*           API Constants        
***************************************/
/**
* \addtogroup group_constants
* @{
*/
    /** \addtogroup driveMode Drive mode constants
     * \brief Constants to be passed as "mode" parameter in the Pin_DVDAC_cap_SetDriveMode() function.
     *  @{
     */
        #define Pin_DVDAC_cap_DM_ALG_HIZ         PIN_DM_ALG_HIZ
        #define Pin_DVDAC_cap_DM_DIG_HIZ         PIN_DM_DIG_HIZ
        #define Pin_DVDAC_cap_DM_RES_UP          PIN_DM_RES_UP
        #define Pin_DVDAC_cap_DM_RES_DWN         PIN_DM_RES_DWN
        #define Pin_DVDAC_cap_DM_OD_LO           PIN_DM_OD_LO
        #define Pin_DVDAC_cap_DM_OD_HI           PIN_DM_OD_HI
        #define Pin_DVDAC_cap_DM_STRONG          PIN_DM_STRONG
        #define Pin_DVDAC_cap_DM_RES_UPDWN       PIN_DM_RES_UPDWN
    /** @} driveMode */
/** @} group_constants */
    
/* Digital Port Constants */
#define Pin_DVDAC_cap_MASK               Pin_DVDAC_cap__MASK
#define Pin_DVDAC_cap_SHIFT              Pin_DVDAC_cap__SHIFT
#define Pin_DVDAC_cap_WIDTH              1u

/* Interrupt constants */
#if defined(Pin_DVDAC_cap__INTSTAT)
/**
* \addtogroup group_constants
* @{
*/
    /** \addtogroup intrMode Interrupt constants
     * \brief Constants to be passed as "mode" parameter in Pin_DVDAC_cap_SetInterruptMode() function.
     *  @{
     */
        #define Pin_DVDAC_cap_INTR_NONE      (uint16)(0x0000u)
        #define Pin_DVDAC_cap_INTR_RISING    (uint16)(0x0001u)
        #define Pin_DVDAC_cap_INTR_FALLING   (uint16)(0x0002u)
        #define Pin_DVDAC_cap_INTR_BOTH      (uint16)(0x0003u) 
    /** @} intrMode */
/** @} group_constants */

    #define Pin_DVDAC_cap_INTR_MASK      (0x01u) 
#endif /* (Pin_DVDAC_cap__INTSTAT) */


/***************************************
*             Registers        
***************************************/

/* Main Port Registers */
/* Pin State */
#define Pin_DVDAC_cap_PS                     (* (reg8 *) Pin_DVDAC_cap__PS)
/* Data Register */
#define Pin_DVDAC_cap_DR                     (* (reg8 *) Pin_DVDAC_cap__DR)
/* Port Number */
#define Pin_DVDAC_cap_PRT_NUM                (* (reg8 *) Pin_DVDAC_cap__PRT) 
/* Connect to Analog Globals */                                                  
#define Pin_DVDAC_cap_AG                     (* (reg8 *) Pin_DVDAC_cap__AG)                       
/* Analog MUX bux enable */
#define Pin_DVDAC_cap_AMUX                   (* (reg8 *) Pin_DVDAC_cap__AMUX) 
/* Bidirectional Enable */                                                        
#define Pin_DVDAC_cap_BIE                    (* (reg8 *) Pin_DVDAC_cap__BIE)
/* Bit-mask for Aliased Register Access */
#define Pin_DVDAC_cap_BIT_MASK               (* (reg8 *) Pin_DVDAC_cap__BIT_MASK)
/* Bypass Enable */
#define Pin_DVDAC_cap_BYP                    (* (reg8 *) Pin_DVDAC_cap__BYP)
/* Port wide control signals */                                                   
#define Pin_DVDAC_cap_CTL                    (* (reg8 *) Pin_DVDAC_cap__CTL)
/* Drive Modes */
#define Pin_DVDAC_cap_DM0                    (* (reg8 *) Pin_DVDAC_cap__DM0) 
#define Pin_DVDAC_cap_DM1                    (* (reg8 *) Pin_DVDAC_cap__DM1)
#define Pin_DVDAC_cap_DM2                    (* (reg8 *) Pin_DVDAC_cap__DM2) 
/* Input Buffer Disable Override */
#define Pin_DVDAC_cap_INP_DIS                (* (reg8 *) Pin_DVDAC_cap__INP_DIS)
/* LCD Common or Segment Drive */
#define Pin_DVDAC_cap_LCD_COM_SEG            (* (reg8 *) Pin_DVDAC_cap__LCD_COM_SEG)
/* Enable Segment LCD */
#define Pin_DVDAC_cap_LCD_EN                 (* (reg8 *) Pin_DVDAC_cap__LCD_EN)
/* Slew Rate Control */
#define Pin_DVDAC_cap_SLW                    (* (reg8 *) Pin_DVDAC_cap__SLW)

/* DSI Port Registers */
/* Global DSI Select Register */
#define Pin_DVDAC_cap_PRTDSI__CAPS_SEL       (* (reg8 *) Pin_DVDAC_cap__PRTDSI__CAPS_SEL) 
/* Double Sync Enable */
#define Pin_DVDAC_cap_PRTDSI__DBL_SYNC_IN    (* (reg8 *) Pin_DVDAC_cap__PRTDSI__DBL_SYNC_IN) 
/* Output Enable Select Drive Strength */
#define Pin_DVDAC_cap_PRTDSI__OE_SEL0        (* (reg8 *) Pin_DVDAC_cap__PRTDSI__OE_SEL0) 
#define Pin_DVDAC_cap_PRTDSI__OE_SEL1        (* (reg8 *) Pin_DVDAC_cap__PRTDSI__OE_SEL1) 
/* Port Pin Output Select Registers */
#define Pin_DVDAC_cap_PRTDSI__OUT_SEL0       (* (reg8 *) Pin_DVDAC_cap__PRTDSI__OUT_SEL0) 
#define Pin_DVDAC_cap_PRTDSI__OUT_SEL1       (* (reg8 *) Pin_DVDAC_cap__PRTDSI__OUT_SEL1) 
/* Sync Output Enable Registers */
#define Pin_DVDAC_cap_PRTDSI__SYNC_OUT       (* (reg8 *) Pin_DVDAC_cap__PRTDSI__SYNC_OUT) 

/* SIO registers */
#if defined(Pin_DVDAC_cap__SIO_CFG)
    #define Pin_DVDAC_cap_SIO_HYST_EN        (* (reg8 *) Pin_DVDAC_cap__SIO_HYST_EN)
    #define Pin_DVDAC_cap_SIO_REG_HIFREQ     (* (reg8 *) Pin_DVDAC_cap__SIO_REG_HIFREQ)
    #define Pin_DVDAC_cap_SIO_CFG            (* (reg8 *) Pin_DVDAC_cap__SIO_CFG)
    #define Pin_DVDAC_cap_SIO_DIFF           (* (reg8 *) Pin_DVDAC_cap__SIO_DIFF)
#endif /* (Pin_DVDAC_cap__SIO_CFG) */

/* Interrupt Registers */
#if defined(Pin_DVDAC_cap__INTSTAT)
    #define Pin_DVDAC_cap_INTSTAT            (* (reg8 *) Pin_DVDAC_cap__INTSTAT)
    #define Pin_DVDAC_cap_SNAP               (* (reg8 *) Pin_DVDAC_cap__SNAP)
    
	#define Pin_DVDAC_cap_0_INTTYPE_REG 		(* (reg8 *) Pin_DVDAC_cap__0__INTTYPE)
#endif /* (Pin_DVDAC_cap__INTSTAT) */

#endif /* CY_PSOC5A... */

#endif /*  CY_PINS_Pin_DVDAC_cap_H */


/* [] END OF FILE */

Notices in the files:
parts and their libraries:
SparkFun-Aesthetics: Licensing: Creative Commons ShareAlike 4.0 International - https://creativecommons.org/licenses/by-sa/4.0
